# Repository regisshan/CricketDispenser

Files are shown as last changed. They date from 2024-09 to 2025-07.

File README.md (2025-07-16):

# About the TG Lab CricketDispenser

If you're here, you're probably interested in the cricket hunting behavior task used by the Turrigiano lab to better understand mechanisms underlying plasticity in the developing visual system. Or maybe you just like throwing crickets at things and want a way to do it remotely.

Designing a containment and distribution system for crickets is surprisingly challenging. This is because crickets are sneaky and squeeze into cracks and crevaces to avoid their inevitable fate. Previous versions of this dispenser had a fatal flaw: crickets could escape the mechanism and fall into the arena at the wrong time, or finding their way into Gina's office where they would give their rather repetitive and chirp-y opinions on grant applications and paper revisions. While cricket chirps are a peaceful background for a fireside chat in the summer, it hits a little close to home when you're staring at a blank word document. Additionally, crickets are shockingly acrobatic and can cling to even the tiniest edge of plastic (think layer lines of a vertical 3d printed wall). 

The new dispenser needed to solve these problems:
* All-or-nothing release (no potential for a half-open chamber where crickets could hide on a tiny ledge)
* Contain the cricket in a glass tube until distribution

Some additional features carried over from the previous version:
*  Motors are distant from the behavior arena to reduce vibration and noise that could alert the mouse/rat where the next cricket will drop
*  Dispensers on opposite corners turn together (so crickets are loaded into every second chamber as a blank)
*  Dispesners are driven by an arduino that is connected to a computer

Anyway, behold: my overly complex cricket dispenser system!
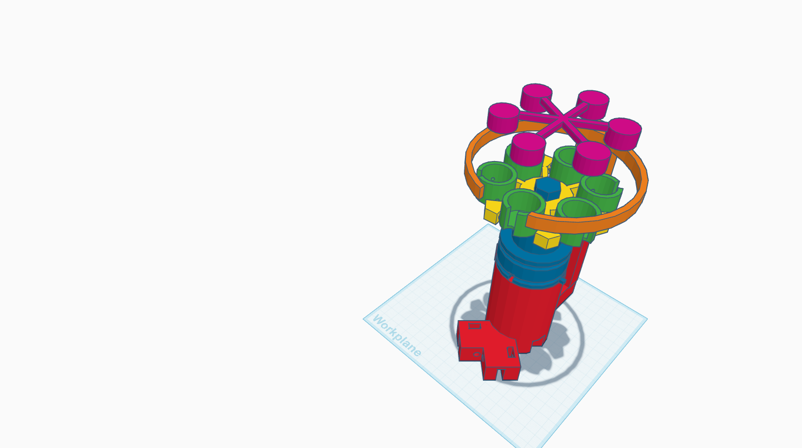
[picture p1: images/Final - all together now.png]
rendering of assembled dispenser


# Obtaining the Materials

3d Print out the following quantites of each print in the 'design files' folder and purchase or obtain materials from dispenser part spreadsheet.

note: one corner setup, which includes a cricket cartridge and dispenser base should be able to print in ~24h on a single print bed on a Prusa i3 MK3S printer. All 4 motor case setups should also print overnight on one print print bed. 

**4x Cricket cartridge**
   - bucket holder
   - 6x glass tube holder
   - hex cap 

**4x Dispenser base**
  - hex holder
  - tall base
  - outer ring

 **4x Motor case**
   - stepper pulley
   - stepper holder
   - tube stick

# Assembling the dispenser

## Assemble the cricket cartridge
The cricket cartridge is the removable part that actually holds the crickets with the glass swinging buckets.

The hexagonal piece has small 3mm round slots where the miniature steel bearings fit. Press fit a small bearing into each of these holes. Insert an undersized dowel pin into the center of each bearing, then squeeze a glass tube holder into each of the 6 spots (you can also leave one spot blank to mark the "0" spot on the cartridge). It might be a good idea to hot glue or super glue the glass tubes into the holders, I have heard some reports of the glass tubes being launched across the arena.

## Assemble the hex holder and dispenser base
The hex holder is the part that sits on the base and spins, where the cricket cartridge sits. 

Press fit a 608-2RS into the bottom of the hex holder. If it doesn't fit, use a heat gun to /gently/ heat the part to soften the plastic, so the bearing can fit inside. 

Put a rubber O-Ring in the slot around the top of the hex holder to dampen the sound of the glass buckets swinging against the part.

Insert a 1" dowel into the hole in the dispenser base. The hex holder should now be able to sit on the base and spin freely. 

Insert two 1/4"-20 nuts into the slot at the bottom of the dispenser holder, then screw in two 1/4"-20 screws through the holes on the side. This will hold the dispenser on the corners of the arena.

Attach the outer ring to the dispenser base by sliding it onto the top of the tower-like piece.

Screw in a push-connector into the hole in the side of the tower-like piece. It is a good idea to glue this in place (superglue works nicely).

Cut some 4mm OD teflon tubing  to the length needed to get from your stepper motors to your dispenser. Thread some braided fishing line through the tubing, with enough extra on either end to wrap around the hex holder and the stepper pulley. Thread the fishing line through the push connector and tie it to the attachment point on the hex holder. Connect the tubing to the push connector. 

## Assemble the motor case

Slide the stepper pulley onto the stepper motor shaft. This will be a tight fit but you want to get the pully down onto the shaft as far as it will go. 

Super glue the tube stick to the stepper holder. Glue the push connector into one of the holes on the tube stick, making sure it is level with the pully when the stepper motor is in the holder. 

Thread the fishing line through the push connector, then tie it to the pulley. attach the tubing to the push connector.

## Assemble the arduino and electronics

Mount the RAMPS shield onto the arduino mega. 

Mount 4 stepper motor drivers onto their spots on the RAMPs board (X, Y, Z, and E), paying attention to the orientation of the drivers vs the RAMPS board. 

Plug in the stepper motors on the RAMPS board.

Plug in the arduino USB and power supply (via the RAMPS board)

Upload the arduino code using the arduino IDE. The code requires the "AccelStepper" package to work
   
# Using the dispenser

With the arduino IDE open, open the serial monitor. A message should appear telling you what buttons to press to advance the motors, and how many steps per turn. If the motors are over or under turning, adjust the number of steps to get it right (I usually see about 40 steps)

# Ideas for future updates
- Integrate with Bonsai
- Use arduino timepoints to cut videos

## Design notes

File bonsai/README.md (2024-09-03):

# Bonsai Files:
## 1. Arduino stepper motor
Controls a stepper motor using a RAMPS V1.4 and XXXX motor drivers. Requires basic firmata protocol to be uploaded to arduino. Ensure baud rate is the same as in the uploaded firmata file.

### pins
X_STEP_PIN         54

X_DIR_PIN          55

X_ENABLE_PIN       38

X_MIN_PIN           3

X_MAX_PIN           2

Y_STEP_PIN         60 

Y_DIR_PIN          61 

Y_ENABLE_PIN       56 

Z_STEP_PIN         46

Z_DIR_PIN          48

Z_ENABLE_PIN       62

Z_MIN_PIN          18

Z_MAX_PIN          19

E_STEP_PIN         26

E_DIR_PIN          28

E_ENABLE_PIN       24

## 2. Arduino servo
Controls servo motors as an alternative to stepper motors - don't need ramps board but servos aren't as strong

## 3. DLC label file
Labels videos with exported DLC model 

## 4. basic dispenser
basic control of the dispenser

## 5. Camera control
basic control of FLIR camera

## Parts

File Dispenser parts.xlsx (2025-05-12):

Item | Vendor | Part number | Qty (in each, not kits!) | link
Printer filament | Hatcbox |  | 2 rolls per setup (different colors if possible) | https://www.amazon.com/s?k=pla+filament&page=2
Polystyrene Plastic Vials, 0.63 FL oz/19 ml Capacity | McMaster-Carr | 4611T32 | too light, delete | https://www.mcmaster.com/4611T32/
DWK Life Sciences Kimble™ ShellVial with N-51A Borosilicate Glass Plain Top | Fisher |  | 64 per setup | https://www.fishersci.com/shop/products/kimble-shellvial-n-51a-borosilicate-glass-plain-top-2/0333932
3x6x2.5 mm Miniature Steel Bearings MR63ZZ L-630 673ZZ Deep Groove Ball Bearing Pack of 10 | Amazon |  | 64 per setup | https://www.amazon.com/JIUWU-3x6x2-5mm-MR63ZZ-L-630-673ZZ/dp/B00ZHSQX42?hvadid=693326160379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
Undersized Dowel Pin | McMaster-Carr | 97049A205 | 64 per setup | https://www.mcmaster.com/97049A205/
Oil-Resistant Buna-N O-Ring 5 mm Wide, 50 mm ID | McMaster-Carr | 9262K842 | 4 per setup | https://www.mcmaster.com/9262K842/
Dowel Pin Alloy Steel, 5/16" Diameter, 1" Long | McMaster-Carr | 98381A583 | 4 per setup | https://www.mcmaster.com/98381A583/
Wellgo 608-2RS Ball Bearings | Amazon |  | 4 per setup | https://www.mcmaster.com/98381A583/
1/4"-20 nut |  |  | 8 per setup
1/4" -20 cap screw |  |  | 8 per setup
Arduino setup
ARDUINO MEGA 2560 REV3 [A000067] | Amazon |  | 1 per setup | https://www.amazon.com/Bearings-Skateboard-Shielded-Miniature-Skateboards/dp/B07R7PR72H?sp_csd=d2lkZ2V0TmFtZT1zcF9hdGY
Chanzon 12V 2A 24W Class 2 Power Supply AC DC Switching Adapter (Input 100-240V, Output 12 Volt 2 Amp) Wall Wart Transformer Charger for DC12V CCTV Camera LED Strip Light (6Ft Cord, 24 Watt Max) | Amazon |  | 1 per setup | https://www.amazon.com/ARDUINO-MEGA-2560-REV3-A000067/dp/B0046AMGW0?ref_=ast_sto_dp
HiLetgo RAMPS 1.4 Control Panel 3D Printer Control Board Reprap Control Board for Arduino Mega 2560 | Amazon |  | 4 per setup | https://www.amazon.com/Chanzon-Switching-Adapter-100-240V-Transformer/dp/B07HNL5D56?s=gateway
MUYI 10 Meters = 32.8 Feet PTFE Teflon Tube OD 4mm ID 2mm for Chemical Electrical Equipment | Amazon |  | depends on location - 1 roll is usually enough | https://www.amazon.com/HiLetgo-Control-Printer-Support-Arduino/dp/B06XZ46PDJ
Twotrees 4 Lead Nema 17 Stepper Motor 42 Motor 1.5A (17HS4401S) with 1m Cable 42BYGH 38MM for CNC/ 3D Printer (Pack of 5) | Amazon |  | 4 motors per setup (nice to have a backup from 5 pack) | https://www.amazon.com/MUYI-Chemical-Electrical-Medical-Equipment/dp/B019PZ5MY4
10 Pieces Stepper Motor Driver Module with Heat Sink Compatible with Stepstick Stepper A4988 3D Printer Reprap, CNC Machine or Robotics | Amazon |  | 4 per setup | https://www.amazon.com/Twotrees-Stepper-17HS4401-Connector-Printer/dp/B07THZQ7RG
Eowpower 10 Pcs PC4-M6 Pneumatic Straight Fitting Joint for Outer Diameter 4mm Nylon Tube, M6 Thread | Amazon |  | 4 per setup | https://www.amazon.com/Stepper-Compatible-Stepstick-Printer-Robotics/dp/B09FQ3G5XQ
 |  |  |  | https://www.amazon.com/Eowpower-Pneumatic-Straight-Fitting-Connector/dp/B01MQYJ9T6
Printed parts

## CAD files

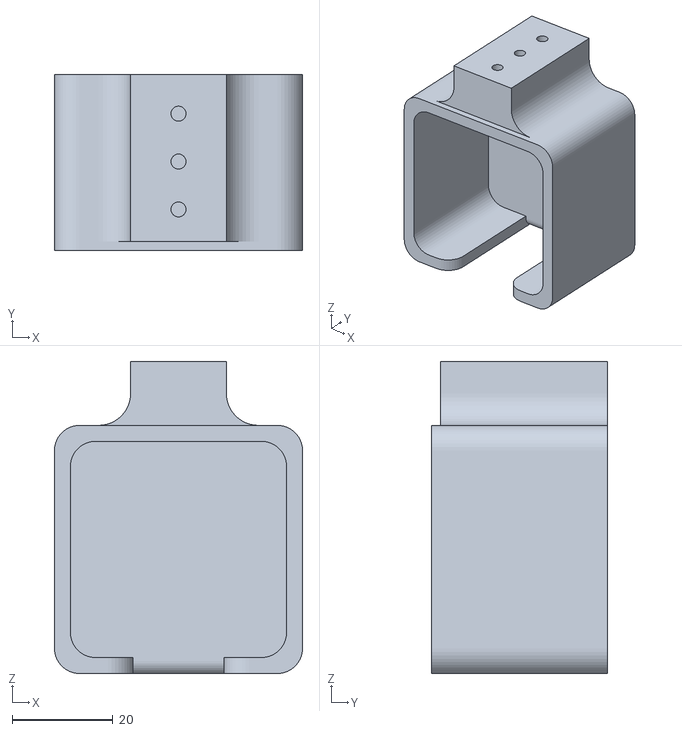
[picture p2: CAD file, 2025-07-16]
design files/stepper holder.stl
49.3 x 34.9 x 62.0

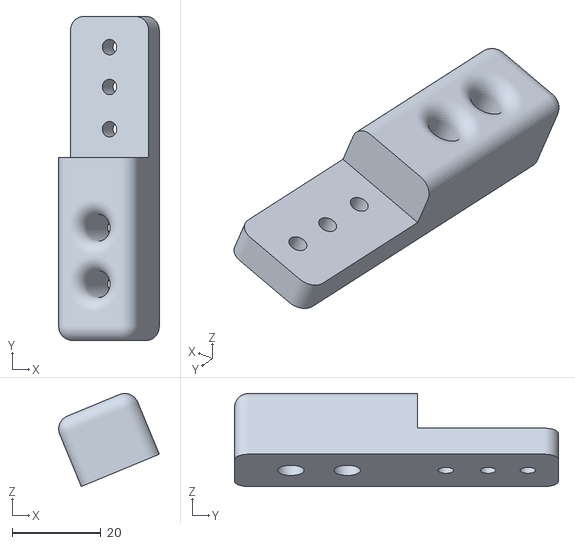
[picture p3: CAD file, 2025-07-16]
design files/tube_stick.stl
22.7 x 73.0 x 21.0

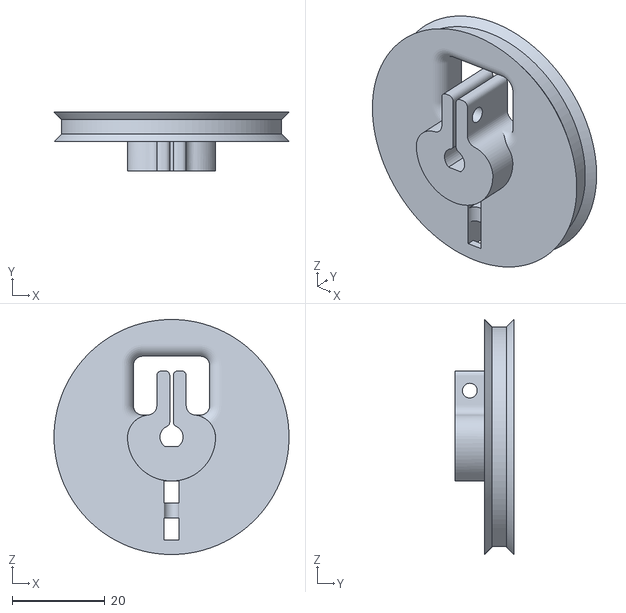
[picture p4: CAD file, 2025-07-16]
design files/stepper pulley.stl
50.8 x 12.7 x 50.8

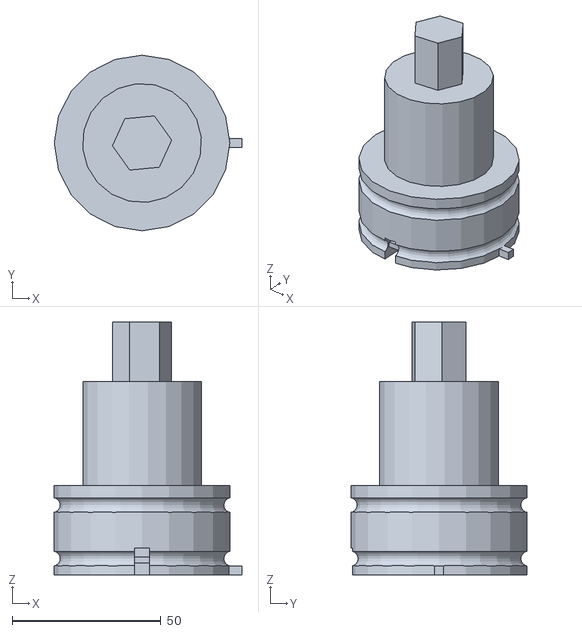
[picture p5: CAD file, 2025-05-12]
design files/hex holder.stl
63.0 x 59.0 x 85.0

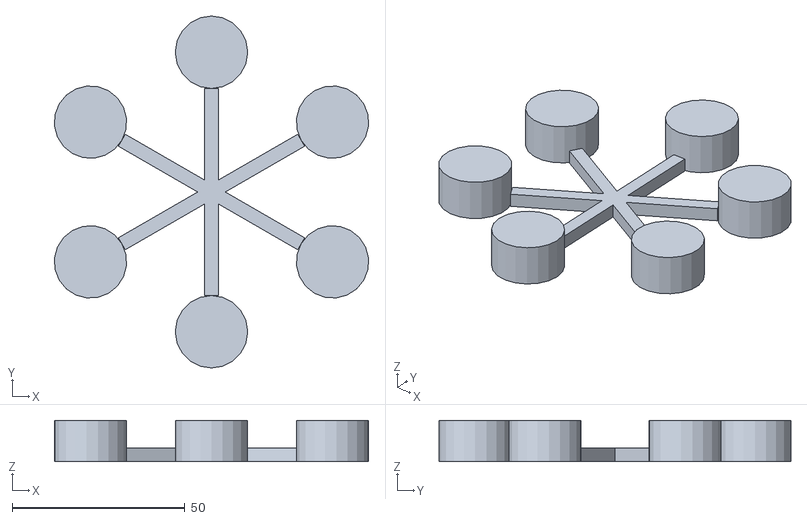
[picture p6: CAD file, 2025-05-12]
design files/Hex cap.stl
91.0 x 102.0 x 12.0

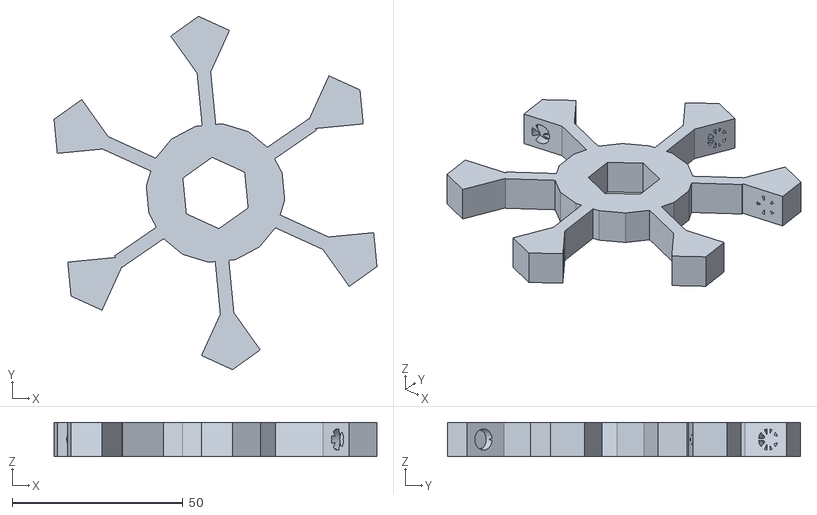
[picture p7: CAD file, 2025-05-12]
design files/bucket holder.stl
94.6 x 103.5 x 10.0

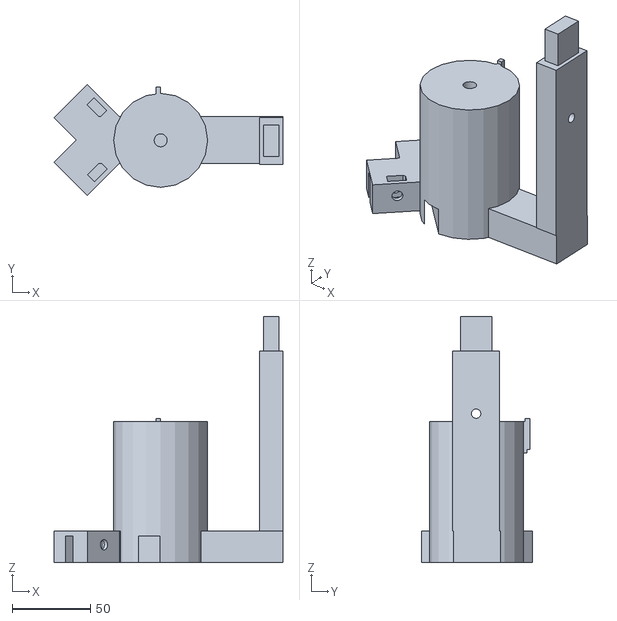
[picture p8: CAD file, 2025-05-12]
design files/tall base.stl
146.0 x 70.9 x 157.0

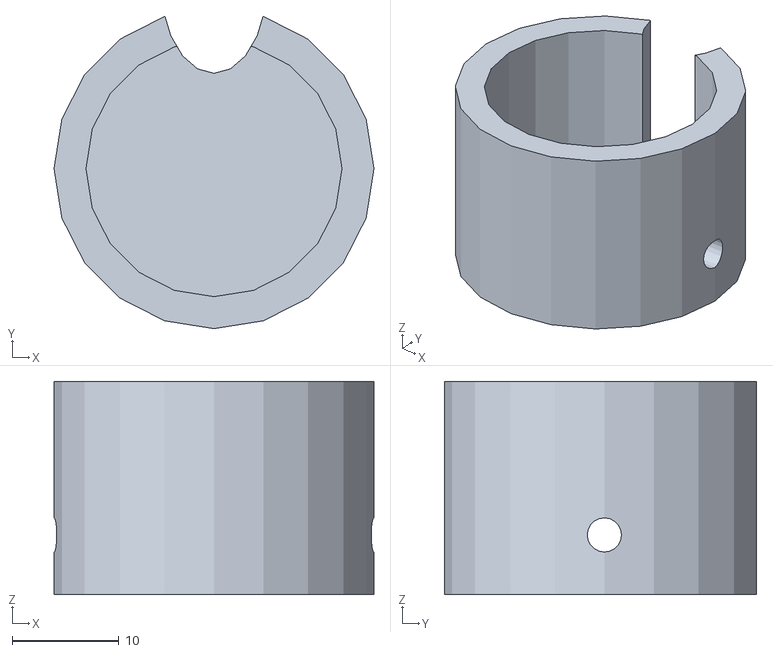
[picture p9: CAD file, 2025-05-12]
design files/glass tube holder.stl
30.0 x 29.3 x 20.0

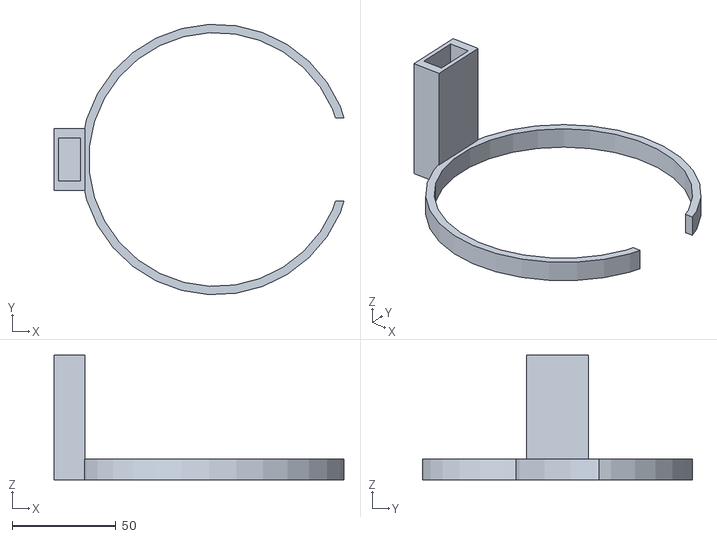
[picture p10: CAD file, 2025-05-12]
design files/outer ring.stl
139.5 x 130.0 x 60.0

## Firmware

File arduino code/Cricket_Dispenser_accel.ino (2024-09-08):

/*
 * RAMPS 1.4: pin for steppers 1, 2, 3, 4
 */
#define X_STEP_PIN         54
#define X_DIR_PIN          55
#define X_ENABLE_PIN       38
#define X_MIN_PIN           3
#define X_MAX_PIN           2

#define Y_STEP_PIN         60 
#define Y_DIR_PIN          61 
#define Y_ENABLE_PIN       56 

#define Z_STEP_PIN         46
#define Z_DIR_PIN          48
#define Z_ENABLE_PIN       62
#define Z_MIN_PIN          18
#define Z_MAX_PIN          19

#define E_STEP_PIN         26
#define E_DIR_PIN          28
#define E_ENABLE_PIN       24

/*
 * Cricket specific numbers
 */
#define num_of_chambers   8
#define full_steps_per_rotation 28 //1.8 deg per full step, 360/1.8=200
//3.942 diameter inside of ridge, 1.875in diameter inside of ridge
#define pulley_ratio (3.942/1.875) //motor is 1/2 the size of chamber
#define microstepping 8 //microstepping mode
#define total_steps_for_rotation  (full_steps_per_rotation*pulley_ratio*microstepping)


#define cricket_per_chamber 7         

#define cricket_pin         11

/*
 * Setup for stepper motors and the different chambers
 */
//#include <Stepper.h>
#include <AccelStepper.h> //ManageLibraries > AccelStepper
 
const int turn = 50; //total_steps_for_rotation/num_of_chambers;//one turn's steps is total steps / number of chambers
//Stepper cricketFeeder[4] = { Stepper(200, X_STEP_PIN, X_DIR_PIN),
//                            Stepper(200, Y_STEP_PIN, Y_DIR_PIN),
//                            Stepper(200, Z_STEP_PIN, Z_DIR_PIN),
//                            Stepper(200, E_STEP_PIN, E_DIR_PIN)};

//AccelStepper stepper[] = {AccelStepper (1, 2, 5), AccelStepper (1, 3, 6)};

AccelStepper cricketFeeder[4] =
  { 
  AccelStepper(AccelStepper::DRIVER, X_STEP_PIN, X_DIR_PIN),   //1
  AccelStepper(AccelStepper::DRIVER, Y_STEP_PIN, Y_DIR_PIN),   //2
  AccelStepper(AccelStepper::DRIVER, Z_STEP_PIN, Z_DIR_PIN),   //3
  AccelStepper(AccelStepper::DRIVER, E_STEP_PIN, E_DIR_PIN)    //4
  };

int turnCounter[2] = {0,
                      0};
bool enabled = HIGH;

void setup() {
  //initializes the 1 chamber's stepper motor
  pinMode(X_STEP_PIN  , OUTPUT);
  pinMode(X_DIR_PIN    , OUTPUT);
  pinMode(X_ENABLE_PIN    , OUTPUT);
  digitalWrite(X_ENABLE_PIN    , LOW);
  
  //initializes the 2 chamber's stepper motor
  pinMode(Y_STEP_PIN  , OUTPUT);
  pinMode(Y_DIR_PIN    , OUTPUT);
  pinMode(Y_ENABLE_PIN    , OUTPUT);
  digitalWrite(Y_ENABLE_PIN    , LOW);

  //initializes the 3 chamber's stepper motor
  pinMode(Z_STEP_PIN  , OUTPUT);
  pinMode(Z_DIR_PIN    , OUTPUT);
  pinMode(Z_ENABLE_PIN    , OUTPUT);
  digitalWrite(Z_ENABLE_PIN    , LOW);

  //initializes the 4 chamber's stepper motor
  pinMode(E_STEP_PIN  , OUTPUT);
  pinMode(E_DIR_PIN    , OUTPUT);
  pinMode(E_ENABLE_PIN    , OUTPUT);
  digitalWrite(E_ENABLE_PIN    , LOW);
  
//initializes the pulse signal for the entire system
   pinMode(cricket_pin, OUTPUT);


   Serial.begin(9600);
   Serial.println("Program Start: enter r or b to turn the steppers 1/3 and 2/4 respectively. \nPress 1,2,3,4 to increment the respective motors a small amount. \nPress d to disable steppers, e to enable steppers.");
   Serial.print("Steps per turn: ");
   Serial.println(turn);
   delay(200);
}

void loop() {


  char input = Serial.read();         //reads serial input for what to do next
  if(input=='d'){
    enabled = LOW;
    digitalWrite(X_ENABLE_PIN    , HIGH);
    digitalWrite(Y_ENABLE_PIN    , HIGH);
    digitalWrite(Z_ENABLE_PIN    , HIGH);
    digitalWrite(E_ENABLE_PIN    , HIGH);
    turnCounter[0]=0;
    turnCounter[1]=0;
    Serial.println("Steppers disabled, resetting chambers");
  }
  if(input=='e'){
    enabled = HIGH;
    digitalWrite(X_ENABLE_PIN    , LOW);
    digitalWrite(Y_ENABLE_PIN    , LOW);
    digitalWrite(Z_ENABLE_PIN    , LOW);
    digitalWrite(E_ENABLE_PIN    , LOW);
    Serial.println("Steppers enabled");
  }
  if(input=='w' && enabled == HIGH){
    Serial.println("white chambers");
    if(turnCounter[0]==cricket_per_chamber){
      Serial.println("Chambers 1&3 are fully turned");
    }else{
      turnTask(0);
      Serial.print("Turning motors 1&3... Turn ");
      turnCounter[0]++;
      Serial.println(turnCounter[0]);
    }
  }
  if(input=='b' && enabled == HIGH){
    Serial.println("blue chambers");
    if(turnCounter[1]==cricket_per_chamber){
      Serial.println("Chambers 2&4 are fully turned");
    }else{
      turnTask(1);
      Serial.print("Turning motors 2&4... Turn ");
      turnCounter[1]++;
      Serial.println(turnCounter[1]);
    }
  }
  if(input=='1'||input=='2'||input=='3'||input=='4'){
    //turnIncrement((int) input - 49); //offset by ascii value of number key?
    Serial.print("incrementing motor ");
    Serial.println(input);
    
  }
}


//void turnTask (int x) {//for normal stepper library
//      sendSignal();
//      cricketFeeder[x].setSpeed(3000);
//      cricketFeeder[x+2].setSpeed(3000);
//      
//      for(int s=0; s<turn/4; s++){
//        cricketFeeder[x+2].step(-4);
//        cricketFeeder[x].step(-4);
//        delay(10);
//      }
//}

void turnTask (int x) {//for accelstepper library
      //Serial.println("turntask");
      sendSignal();
      setStepperDefaults(x);
      //Serial.println(turn);
      cricketFeeder[x].setCurrentPosition(0); //set current position as zero
      cricketFeeder[x+2].setCurrentPosition(0); //set current position as zero
      //Serial.println(cricketFeeder[x].distanceToGo());
      cricketFeeder[x].moveTo(turn);
      cricketFeeder[x+2].moveTo(turn);
      //Serial.println(cricketFeeder[x].distanceToGo());
      while(cricketFeeder[x].distanceToGo() > 0)
      {
        cricketFeeder[x].run();
        cricketFeeder[x+2].run();
      }
}
void setStepperDefaults(int x){
    cricketFeeder[x].setMaxSpeed(100.0); //200 is default
    cricketFeeder[x+2].setMaxSpeed(100.0); //200 is default,
    cricketFeeder[x].setAcceleration(50.0); //100 is default
    cricketFeeder[x+2].setAcceleration(50.0); //100 is default
}

//void turnIncrement(int x){
//  sendSignal();
//  cricketFeeder[x].setSpeed(10);
//  cricketFeeder[x].step(-10);
//}


/*
 * Sends signal to the main board for logging when a cricket is dropped
 */
void sendSignal (){
    digitalWrite(cricket_pin, HIGH);
    delay(200);
    digitalWrite(cricket_pin, LOW);
}

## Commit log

2024-08-20 Rename chamber holder (4).stl to design files/chamber holder.stl
    [chamber holder.stl]
2024-08-20 Rename chamber ring (3).stl to design files/chamber ring.stl
    [chamber ring.stl]
2024-08-29 Update and rename arduino servo.bonsai to bonsai/arduino servo.bonsai
2024-08-29 Update and rename camera control.bonsai to bonsai/camera control.bonsai
2024-09-08 Update and rename Cricket_Dispenser_accel.ino to arduino code/Cricket_Dispenser_accel.ino
